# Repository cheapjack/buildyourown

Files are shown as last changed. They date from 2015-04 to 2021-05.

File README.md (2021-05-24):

# DesktopProsthetics
### 4th June - 31st August 2015 at [FACT](https://www.fact.co.uk/artwork/desktop-prosthetics-2015)
**Gallery 1, FACT, 88 Wood Street, Liverpool, L1 4DQ**

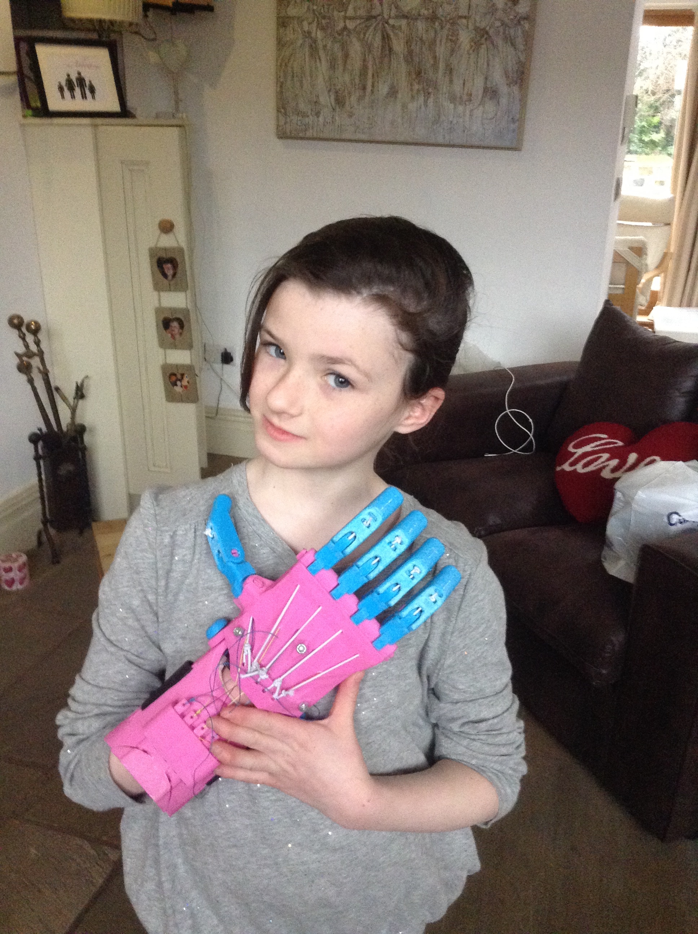
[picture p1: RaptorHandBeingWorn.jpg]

Image Copyright Jason Abbott.
### Copy:

###[DoESLiverpool](http://doesliverpool.com "DoESLiverpool's Homepage") will develop an iteration of the [Enabling the Future](http://enablingthefuture.org/upper-limb-prosthetics/the-raptor-hand/ "Enabling The Future Website") project within the Build Your Own Show at FACT. DoESLiverpool is a community of makers and entrepreneurs in Liverpool, with a Co-Working space, Workshop and Event Hub. It’s a place to work, learn, share ideas, form groups and make things the way you want to for small fees or initially, cake.

###DoES will be lead creative technologists to help setup, facilitate and support a ‘production line’ area for Build Your Own introducing the idea of 3D printing open source designs of upper limb prosthetics. It's inspired by a local family who used DoESLiverpool's workshop to print hand parts independently.

###Over the course of the exhibition FACT Gallery Assistants and DoESLiverpool will assist the public in testing and building 3D printed prosthetic devices. The public will have the opportunity to play, experiment and understand what prosthetics are and how access to rapid prototyping and open source digital making tools can help people make the world the way they want it.

## Information on this Repository:

Project management, help and files for the 3D printed prosthetic hand project
* *Most questions* [answered on our Frequently Asked Questions Page](https://github.com/cheapjack/buildyourown/blob/master/FAQ.md) which is being updated as needs arise.
* [Issues](https://github.com/cheapjack/buildyourown/issues "github issues for the project") to aid @cheapjack @amcewen and @defproc management of the project and information
* [copy as README.md files](https://github.com/cheapjack/buildyourown/tree/master/events) for publicity in the events folder
* Other useful information and files like model parts

We are also collecting related information - links, pictures, etc. - over on the [Desktop Prosthetics tumblr](http://desktopprosthetics.tumblr.com/)

### Issues:

The issue list is a place to track what needs to be done.  Creating and closing them is cheap, so make liberal use of them :-)

It's easy to see which issues need addressing by looking at the [open issue list](https://github.com/cheapjack/buildyourown/issues) but there are other ways to slice and dice things.  Issues get [labelled](https://github.com/cheapjack/buildyourown/labels) as a way to group them together - feel free to create new labels as and when needed.  And there are a few [milestones](https://github.com/cheapjack/buildyourown/milestones) to mark when issues have to be finished.  Use milestones for things that '''have''' to be done before a set event, rather than for "it'd be lovely if this was done by date X", as that just clutters things up if the deadline isn't hit.

Some more useful labels:
 * [Exhibits](https://github.com/cheapjack/buildyourown/labels/Exhibits)  Anything relating to the exhibits themselves
 * [Graphics](https://github.com/cheapjack/buildyourown/labels/Graphics)  Anything relating to the wall text, images, and data visualisation
 * [Set design](https://github.com/cheapjack/buildyourown/labels/Set%20design)  Issues relating to the 3d design of the exhibition
 * [Liverpool](https://github.com/cheapjack/buildyourown/labels/Liverpool)  Anything related specifically to the exhibition at FACT
 * [Norwich](https://github.com/cheapjack/buildyourown/labels/Norwich)  Anything related specifically to the exhibition at Norwich Castle

For some more background on good practice when using issues, read http://ben.balter.com/2014/11/06/rules-of-communicating-at-github/.  It's about Github's culture and process rather than exactly how we're running things, but there's plenty of crossover.

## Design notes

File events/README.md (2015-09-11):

## Files and copy for events as .md files per event

### Refer to the [Calendar](http://bit.ly/prostheticscal "Link to calendar for events at DesktopProsthetics, note the scal bit") for latest dates and times

FACT Liverpool events:
 * [Measuring Up](MeasuringUpWorkshop.md) **Saturday 6th June** 
 * [What's your superpower? A Prosthetic Hack!](ProstheticHack.md) **Saturday 25th July** [FACT link](http://fact.co.uk/whats-on/current/does-what-s-your-super-power-a-prosthetic-hack.aspx) 
 * [Assembly workshop](Assemblyworkshop.md) **Saturday 8th August** & **Saturday 22nd August**
 * [DoES does Prosthetics Day](https://github.com/cheapjack/buildyourown/blob/master/events/DoESdoesProsthetics.md) at DoES Liverpool **Saturday 15th August 2015** 
 * [DoES does Prosthetics Day 2](https://github.com/cheapjack/buildyourown/blob/master/events/DoESdoesProsthetics2.md) at DoES Liverpool **Saturday 17th October 2015** 
* [x] event dates signed off

**Norwich Castle events to be defined, arranged, etc. by the Norwich partners.**

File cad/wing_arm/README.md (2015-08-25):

### Wing and RIT-Arm models

src files for the Wing and RIT-Arm experimnets

#### Notes

I'm not sure what's best way of scaling? **eg** I've found if I take the generated `undies-manual`, and I scale it by 1.2 uniformly as below it 'looks' right in Openscad:

```
//joint interface

wingscalar = 1.2;

scale([wingscalar,wingscalar,wingscalar])translate([wingposx, wingposy, wingposz])import ("/Users/Power5/buildyourown/cad/experiments/RaptorWingAdaptiveGripExperiment/elbow_joint_interface_right.stl", convexity = 3);

```

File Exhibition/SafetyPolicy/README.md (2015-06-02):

# Safety Policy and Other Guidelines

## Place for safety guidelines from e-NABLE

### e-NABLE Device Safety Guidelines Statement

Based on preliminary testing and observations on the functionality and capabilities of our experimental 3D printed prosthetic devices it is felt that they are currently not safe for operation of heavy machinery, tools, equipment, and vehicles due to low grip strength development. These prosthetic devices have shown, however, to provide some functionality for gross grasp activities of light and pliable objects, but it is in no way a substitute for a fully functioning hand. In addition, we don’t recommend the use of our experimental 3D printed prosthetic devices for small children (i.e., under 3 years of age) due to greater fall rate and the need of sensory input through oral stimulation. Furthermore, it is unknown if our experimental 3D printed prosthetic devices are able to sustain a small child’s bite without breaking. Please review and consider the following recommendations and precautions regarding the 3D printed prosthetic device

### General Recommendations for experimental 3D printed prosthetic device

### Physical Safety

 * Work with your doctor or medical professional for appropriate use and wearing schedule of your experimental 3D printed prosthetic device.
 * These devices are made with low temperature plastic and should not be exposed to temperatures over 120° degrees.  A 3D printed prosthetic device left in a car on a hot day may be damaged.
 * With any prosthetic there is a possibility to develop pressure sores. If redness develops after wearing for the 15-20 minute trial please contact provider of the device, to reevaluate fit. If redness persists please contact your healthcare provider.
 * Monitor your device for wear and tear and contact your provider for assistance with replacing worn or broken parts.
 * Users should assume that the device could break at any moment, even while using it for tasks that have worked in the past, because the rate at which the plastic parts fatigue and need to be replaced is unknown.
 * Do not use the device to lift boiling water off the stove (e.g. cooking pasta) or to lift dishes of very hot food out of a microwave oven or out of a hot oven or any other situation in which a failure of the experimental device could cause injury indirectly if the hot material is dropped or spilled.

### Health Safety

 * Allow the mechanical hand breathing room as excessive sweat and other components may cause poor hygiene and lead to skin problems.
 * The use of a prosthetic sock is recommended for individuals with sensitive skin.
    Make sure you have no allergic reactions to the material used to print the mechanical hand or any other component.
    Make sure the mechanical hand is comfortable.
    Ensure the mechanical hand is functioning for the correct purpose.
    Start using the hand in a progressive manner. If the muscles of your wrist joint are tired, it would be a good idea to take a break and continue using the mechanical hand the next day.

### Child Safety

 * The child needs to be supervised at all times while using these mechanical hands.
 * Young children cannot be trusted to watch out for the Health Safety items listed above.  It is the responsibility of the caretaker to check for any problems with the child using an experimental 3D printed prosthetic device.
 * Let the child use/play with the device in a very conservative, progressive schedule:  just 5-10 minutes at a time, or even less.  If the child likes the device and is eager to use it, let them work up to using it for longer periods of time gradually.  Talk with a pediatrician or other medical professional about how much use is safe for the child, and what other problems to watch out for.
 * If your child feels pain on the wrist or elbow joint, please stop using the mechanical hand. This may be a sign of an overuse injury.
 * If any component of the mechanical hand breaks, please stop using it.
 * Ensure that the hardware and other moving parts are not loose, especially for children young enough to be at risk of choking on foreign objects.
 * The use of the 3D printed prosthetic device should be coordinated with the child’s teacher and health care providers.
 * The 3D printed prosthetic device is not made for weight-bearing or supporting body weight, so outdoor or rough play with the prosthetic should be closely monitored.
 * Children who are not walking or are unsteady on their feet may not be appropriate for this device as falling on the 3D printed prosthetic device may result in further injury.

### Cleaning instructions:

The 3D printed prosthetic device can be surface cleaned with warm water and a mild detergent.  If an odor develops on the device, cleaning with shaving cream may help to dissipate the odor.  If Velcro straps become worn or ineffective, please contact the provider of your prosthetic hand for replacement.

### DesktopProsthetics, DoES Liverpool & FACT Release and Waiver of Liability and Hold Harmless Agreement:

You acknowledge that you understand the context of the **DoESLiverpool CIC** and **FACT** project **"Desktop Prosthetics"** that uses the open source design "Raptor Hand Reloaded" from the e-NABLE Community Foundation (“Foundation”); a non-profit foundation to encourage the development and dissemination of prosthetics for children and adults using 3D printing technology. 
**DoESLiverpool CIC ("DoESLiverpool")** and **FACT (Foundation for Art and Creative Technology) ("FACT") generally **do not** create the design or plans (“Designs”) **but**  print the components, assemblies and final prototype prosthetics based on the Designs (“Components”), They **do not** certify that the Designs or Components or assembled prototype prosthetics operate properly or satisfy any regulatory requirements.

Members of the DoESLiverpool Community, FACT Gallery Guides and a community of people around the **DesktopProsthetics** project following a Measuring Workshop agree to use the assembled components as prototype prosthetics, 3D printed at the DesktopProsthetics exhibition at the FACT show "Build Your Own: Tools for sharing" and follow all recommendations and safety guidelines here.

This Release and Waiver of Liability and Hold Harmless Agreement (“Agreement”) is meant to reflect the limited role of DoESLiverpool and FACT in the development and manufacture of the Design and Components and subsequent assembled prototype prosthetics. The person signing below (“You”) is either the individual recipient of the Design or Component if the individual recipient is an adult under the laws of the relevant jurisdiction or the parent or legal guardian of the child if the individual recipient is a child under the laws of the relevant jurisdiction.

You agree that any Design or Component furnished to me by the DesktopProsthetics project or by any individual associated with DoESLiverpool and FACT is provided “AS IS” and **without representations or warranties of any kind, express or implied, and is intended to be a gift**.  By accepting any Design or Component, I further acknowledge that such Design or Component, has not been evaluated or approved by any regulatory authority.  Generally, the Design has been developed by a person or a company who may be a member of the e-NABLE community, DoESLiverpool or FACT but is not an employee or contractor of the above. 

You understand that any Design, Assembled prototype prosthetic or Component furnished by the DesktopProsthetics is meant to benefit an individual recipient who has need of an assistive hand technology, and is not intended, and shall not be used, for commercial use.  If You are an adult under the laws of the relevant jurisdiction and are the individual recipient, You acknowledge that You understand the potential risks of the use of the Design or Component and expressly assume such risks.  If the individual recipient is a child under the laws of the relevant jurisdiction, You represent that You are the parent or legal guardian of the child and that You understand the potential risks of the use of the Design or Component and expressly assume such risks on behalf of the individual recipient.

Furthermore, You (either for yourself or your child)  release and forever discharge DoESLiverpool and FACT and their  officers, employees, contractors, subcontractors, volunteers and agents (“Releasees”) from any and all liability for acts or omissions— including negligent acts or omissions—causing damage, loss, injury, or death to the individual recipient from the use of the Design or the Component. You agree to defend, indemnify and hold the Releasees harmless from any and all liability or loss— including liability for negligence—arising in conjunction with or resulting from the individual recipient’s use of a Design or Component (including all legal/representation fees and expenses incurred by the Releasees).

You further understand and agree that the Foundation and any individual associated with the Foundation shall not be liable for any injuries or damages, including any consequential, incidental, indirect, punitive or special damages, resulting from or arising out of the use of the Design or Component provided by DoESLiverpool, FACT or any individual associated with the associated parties.

Any information provided by DoESLiverpool and any individual associated is not intended to be used or relied upon to diagnose or treat a health problem or disease and DoESLiverpool makes no claims regarding the Design or the Components.  You should consider consulting with a qualified health care provider prior to fitting the Component.  Carefully read all labels and heed all directions and cautions that accompany the Components.  Any statements made by DoESLiverpool are for informational purposes only and are not meant to replace the services or recommendations of a physician or other qualified health care practitioner.

You acknowledge that this Agreement is governed by UK law (without reference to its conflict of law provisions) and the parties intend that this Agreement to be as broad and inclusive as permitted by UK law. If any portion of this Agreement is found to be invalid for any reason, the remainder of the Agreement shall continue to remain in full force and effect and shall continue to be binding in all cases.

You have carefully read the foregoing provisions and understand their contents.

Signed

Signature  ______________________  Print Name  ___________________________ Date:__________

### e-NABLE Release and Waiver of Liability and Hold Harmless Agreement:

You acknowledge that you understand that the e-NABLE Community Foundation (“Foundation”) is a non-profit foundation to encourage the development and dissemination of prosthetics for children and adults using 3D printer technology.  The Foundation generally does not create the design or plans (“Designs”) nor manufacture or print the components, assemblies or final prosthetics based on the Designs (“Components”), nor does it certify the Designs or Components operate properly or satisfy any regulatory requirements.  This Release and Waiver of Liability and Hold Harmless Agreement (“Agreement”) is meant to reflect the limited role of the Foundation in the development of the Design and Components. The person signing below (“You”) is either the individual recipient of the Design or Component if the individual recipient is an adult under the laws of the relevant jurisdiction or the parent or legal guardian of the child if the individual recipient is a child under the laws of the relevant jurisdiction.

You agree that any Design or Component furnished to me by the Foundation or by any individual associated with the Foundation is provided “AS IS” and without representations or warranties of any kind, express or implied, and is intended to be a gift.  By accepting any Design or Component, I further acknowledge that such Design or Component, has not been evaluated or approved by any regulatory authority.  Generally, the Design has been developed by a person or a company who may be a member of the e-NABLE community but is not an employee or contractor of the Foundation. Similarly, the Component has generally not been manufactured or printed by a person or company who is a member of the e-NABLE community but once again is not an employee or independent contractor of the Foundation.

You understand that any Design or a Component furnished by the Foundation is meant to benefit an individual recipient who has need of an assistive hand technology, and is not intended, and shall not be used, for commercial use.  If You are an adult under the laws of the relevant jurisdiction and are the individual recipient, You acknowledge that You understand the potential risks of the use of the Design or Component and expressly assume such risks.  If the individual recipient is a child under the laws of the relevant jurisdiction, You represent that You are the parent or legal guardian of the child and that You understand the potential risks of the use of the Design or Component and expressly assume such risks on behalf of the individual recipient.

Furthermore, You (either for yourself or your child)  release and forever discharge the Foundation and its  officers, employees, contractors, subcontractors, volunteers and agents (“Releasees”) from any and all liability for acts or omissions— including negligent acts or omissions—causing damage, loss, injury, or death to the individual recipient from the use of the Design or the Component. You agree to defend, indemnify and hold the Releasees harmless from any and all liability or loss— including liability for negligence—arising in conjunction with or resulting from the individual recipient’s use of a Design or Component (including all attorney’s fees and expenses incurred by the Releasees).

You further understand and agree that the Foundation and any individual associated with the Foundation shall not be liable for any injuries or damages, including any consequential, incidental, indirect, punitive or special damages, resulting from or arising out of the use of the Design or Component provided by the Foundation or any individual associated with the Foundation.

Any information provided by the Foundation and any individual associated with the Foundation is not intended to be used or relied upon to diagnose or treat a health problem or disease and the Foundation makes no claims regarding the Design or the Components.  You should consider consulting with a qualified health care provider prior to fitting the Component.  Carefully read all labels and heed all directions and cautions that accompany the Components.  Any statements made by the Foundation are for informational purposes only and are not meant to replace the services or recommendations of a physician or other qualified health care practitioner.

You acknowledge that this Agreement is governed by the laws of the State of Delaware (without reference to its conflict of law provisions) and the parties intend that this Agreement to be as broad and inclusive as permitted by law. If any portion of this Agreement is found to be invalid for any reason, the remainder of the Agreement shall continue to remain in full force and effect and shall continue to be binding.

You have carefully read the foregoing provisions and understand their contents.

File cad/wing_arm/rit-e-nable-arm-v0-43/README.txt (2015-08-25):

Arm.iam is the master assembly Inventor file.

The other files are subassemblies required by Arm.iam, and open-able independently.

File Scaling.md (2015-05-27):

## Linear Scaling 

The main measurement used in sizing the Raptor Reloaded is the width of the recipient's complete hand at the knuckles. At 100% scale, the palm of the Raptor Reloaded measures 55mm at its widest point. To get the appropriate linear scaling factor for scaling the STLs, add 5mm (to account for the thickness of padding in the printed palm) to the width of the recipient's complete hand at its widest point. Divide this number by 55 to get the scaling factor for the STLs. For example, if the palm is 65mm wide, then 65 + 5 = 70, and 70 / 55 = 1.27, so the scaling multiplier would be 1.27 or 127%. Make sure to apply the scaling factor to all of the parts to ensure that they fit together. At higher scales, the clearances between the moving parts of the hand will grow, so glue or other modifications may be necessary to ensure that all the pieces stay secured to each other.

## Recommended Printing Settings

 * PLA (or ABS, PET, Nylon)
 * 0.2mm layers
 * 0.8mm shell thickness (2 shells)
 * 35% infill
 * Active cooling fan on

## Additional Materials

The Raptor Reloaded requires some additional hardware to assemble, most of which can be sourced from the Hardware Sources page on the e-NABLE website.

 * 4ft Velcro, double-sided (2” wide)
 * 8ft Non-elastic nylon cord, 0.9mm-1.0mm
 * 5ft Flexible elastic cord
 * 5x Tensioner screws (*it's no clear which size these should be*) 
 * 4x Palm velcro attachment screws
 * 12" (305mm) Firm Foam Padding (5 ¾” wide)
 * 5x Lee Tippi Micro Gel Fingertip Grips (optional)

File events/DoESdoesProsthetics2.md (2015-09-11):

# DoES does Prosthetics Day 2

Baylee & Jason printing for the BBC no.2

### Saturday 17th October 2015 12.30pm - 4pm
### DoESLiverpool, The Gostins Building, 4th Floor, left from lift, 32-36 Hanover Street. Liverpool L1 4LN

#### Free no booking required

### Meeting following on from the **DesktopProsthetics** project

**Age 3 and above, children accompanied by an adult**
#### DoESLiverpool and project participnats will be helping Assemble, test, adjust and fit more printed hands from the DesktopProsthetics Project

## Workshop activity
* Re-Introduction to project
* Re-Connecting to e-NABLE
* Learning how to assemble a raptor hand
* Test and fit hands
* Log any issues and improvements required for the hands
* Propose another meet up and discuss ways of sustaining the community; and basics of communication using either Google Groups or [Meetup](http://www.meetup.com/)

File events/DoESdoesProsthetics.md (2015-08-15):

# DoES does Prosthetics Day

Baylee & Jason printing for the BBC

### Saturday 15th August 2015 12.30pm - 4pm
### DoESLiverpool, The Gostins Building, 4th Floor, left from lift, 32-36 Hanover Street. Liverpool L1 4LN

#### Free no booking required

### Meeting following on from the Measuring, Hacking and Assembly workshops for **DesktopProsthetics**

**Age 3 and above, children accompanied by an adult**
#### DoESLiverpool and project participnats will be helping Assemble, test, adjust and fit more printed hands from the DesktopProsthetics Project

## Workshop activity
* Re-Introduction to project
* Connecting to e-NABLE
* Learning how to assemble a raptor
* Test and fit hands
* Log any issues and improvements required for the hands
* Propose another meet up and discuss running an interest group / club or Prosthetic Evenings/Saturdays

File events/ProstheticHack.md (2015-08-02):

# What's Your SuperPower? - A Prosthetic Hack!

[Book on the FACT website here](http://fact.co.uk/whats-on/current/does-what-s-your-super-power-a-prosthetic-hack.aspx)

Image source [Enabling the Future on Thingiverse](http://thingiverse-production-new.s3.amazonaws.com/renders/1d/20/95/d4/49/All_parts_at_100_right_single_build_plate_preview_featured.jpg) Licensed under [Attribution-ShareAlike 3.0 Unported (CC BY-SA 3.0)](http://creativecommons.org/licenses/by-sa/3.0/ "License Link")

## Saturday 25th July FACT Gallery 1 12pm-4.30pm FREE
**Age 3 and above, children accompanied by an adult**

## DoESLiverpool will be hosting a prosthetic hackday exploring how the **DesktopProsthetics** project, part of Build Your Own, can be hacked and modified to explore the diversity of prosthetic design. 
### The Raptor hand used in **DesktopProsthetics** is a general pick up and place prosthetic but with rapid prototyping tools like 3D printing can we develop modifications or 'hacks' for the reality of unique users? What prosthetics could we make for hiphop MC's, dancers, mathematicians, event organisers, farmers, gallery assistants or engineers?  We will explore prosthetic hand design as a group then prototype and present our co-designs.

We will also be looking at how to adapt the Raptor Re-Loaded for those families with no conventional working wrist joint. Take part in co-design and simple making activity and explore 3D generation tools from [OpenSCAD](http://www.openscad.org/) to **Lego®** 

http://enablingthefuture.org/upper-limb-prosthetics/the-raptor-hand/
http://doesliverpool.com

 * [x] Copy signed off

### Workshop Activity
* Look at prosthetic design
* Explore unique user applications
* Explore human centred and activity centred co-design
* Modify and prototype new designs
* Explore different design tools
* Present & document prototypes, printing where possible.

### Prep
 * Try adding some Lego connectors to a hand and print it out.  [Parametric Lego model in OpenSCAD](http://www.thingiverse.com/thing:178627)
 * Increase height of Top-side Lego 'teeth' in [OpenSCAD](http://www.openscad.org/) for better fit with **official LEGO®**
 * Print a few part from the [Universal Construction Kit](http://www.thingiverse.com/uck/designs) for fun
 * Find a few compatible *other building systems* to fit the UCK stuff
 * Have an instance of OnShape to play with
 * Have the Printcraft server for young people to play on
 * Simple examples of using [OpenSCAD](http://www.openscad.org/)
 * Source some FACT laptops (say 2)

### Checklist

 * [ ] Wallpaper cover paper
 * [ ] Masking Tape
 * [ ] Pens & Paper
 * [ ] Superglue
 * [ ] Post-it Notes
 * [ ] Freshly Printed Lego Finger adaptors
 * [ ] OnShape
 * [x] OpenSCAD
 * [x] Lego technic
 * [x] 2 MacBooks (FACT)
 * [x] Flipchart (FACT)
 * [x] Minecraft (FACT)

### Background Information
 * http://rewalk.com/rewalk-personal-3/
 * http://www.theguardian.com/artanddesign/architecture-design-blog/2015/jul/22/lego-prosthetic-arm-that-kids-can-hack-themselves
 * http://www.openbionics.org/
 * http://news.harvard.edu/gazette/story/2015/06/a-new-grasp-on-robotic-glove/
 * http://www.engadget.com/2015/03/13/3d-printed-iron-man-gauntlet-becomes-a-kids-awesome-bionic-arm/

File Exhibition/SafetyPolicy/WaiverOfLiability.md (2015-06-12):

## DesktopProsthetics, DoES Liverpool & FACT Safety Guidelines 
## Release & Waiver of Liability and Hold Harmless Agreement

If you are taking part in the **measuring workshop** on the **6th June 2015** at **FACT**, Liverpool, you agree to read, sign and keep a copy of the following **Safety Guidelines** provided by **e-NABLE** the source of the **Raptor-Reloaded prosthetic prototype design** and the **DoESLiverpool** and **FACT Waiver of Liability agreement** 

### e-NABLE Device Safety Guidelines Statement

Based on preliminary testing and observations on the functionality and capabilities of our experimental 3D printed prosthetic devices it is felt that they are currently not safe for operation of heavy machinery, tools, equipment, and vehicles due to low grip strength development. These prosthetic devices have shown, however, to provide some functionality for gross grasp activities of light and pliable objects, but it is in no way a substitute for a fully functioning hand. In addition, we don’t recommend the use of our experimental 3D printed prosthetic devices for small children (i.e., under 3 years of age) due to greater fall rate and the need of sensory input through oral stimulation. Furthermore, it is unknown if our experimental 3D printed prosthetic devices are able to sustain a small child’s bite without breaking. Please review and consider the following recommendations and precautions regarding the 3D printed prosthetic device

### General Recommendations for experimental 3D printed prosthetic device

### Physical Safety

 * Work with your doctor or medical professional for appropriate use and wearing schedule of your experimental 3D printed prosthetic device.
 * These devices are made with low temperature plastic and should not be exposed to temperatures over 120° degrees.  A 3D printed prosthetic device left in a car on a hot day may be damaged.
 * With any prosthetic there is a possibility to develop pressure sores. If redness develops after wearing for the 15-20 minute trial please contact provider of the device, to reevaluate fit. If redness persists please contact your healthcare provider.
 * Monitor your device for wear and tear and contact your provider for assistance with replacing worn or broken parts.
 * Users should assume that the device could break at any moment, even while using it for tasks that have worked in the past, because the rate at which the plastic parts fatigue and need to be replaced is unknown.
 * Do not use the device to lift boiling water off the stove (e.g. cooking pasta) or to lift dishes of very hot food out of a microwave oven or out of a hot oven or any other situation in which a failure of the experimental device could cause injury indirectly if the hot material is dropped or spilled.

### Health Safety

 * Allow the mechanical hand breathing room as excessive sweat and other components may cause poor hygiene and lead to skin problems.
 * The use of a prosthetic sock is recommended for individuals with sensitive skin.
    Make sure you have no allergic reactions to the material used to print the mechanical hand or any other component.
    Make sure the mechanical hand is comfortable.
    Ensure the mechanical hand is functioning for the correct purpose.
    Start using the hand in a progressive manner. If the muscles of your wrist joint are tired, it would be a good idea to take a break and continue using the mechanical hand the next day.

### Child Safety

 * The child needs to be supervised at all times while using these mechanical hands.
 * Young children cannot be trusted to watch out for the Health Safety items listed above.  It is the responsibility of the caretaker to check for any problems with the child using an experimental 3D printed prosthetic device.
 * Let the child use/play with the device in a very conservative, progressive schedule:  just 5-10 minutes at a time, or even less.  If the child likes the device and is eager to use it, let them work up to using it for longer periods of time gradually.  Talk with a pediatrician or other medical professional about how much use is safe for the child, and what other problems to watch out for.
 * If your child feels pain on the wrist or elbow joint, please stop using the mechanical hand. This may be a sign of an overuse injury.
 * If any component of the mechanical hand breaks, please stop using it.
 * Ensure that the hardware and other moving parts are not loose, especially for children young enough to be at risk of choking on foreign objects.
 * The use of the 3D printed prosthetic device should be coordinated with the child’s teacher and health care providers.
 * The 3D printed prosthetic device is not made for weight-bearing or supporting body weight, so outdoor or rough play with the prosthetic should be closely monitored.
 * Children who are not walking or are unsteady on their feet may not be appropriate for this device as falling on the 3D printed prosthetic device may result in further injury.

### Cleaning instructions:

The 3D printed prosthetic device can be surface cleaned with warm water and a mild detergent.  If an odor develops on the device, cleaning with shaving cream may help to dissipate the odor.  If Velcro straps become worn or ineffective, please contact the provider of your prosthetic hand for replacement.

## DesktopProsthetics, DoES Liverpool & FACT Release and Waiver of Liability and Hold Harmless Agreement:

You acknowledge that you understand the context of the **DoESLiverpool CIC** and **FACT** project **"Desktop Prosthetics"** that uses the open source design "Raptor Hand Reloaded" from the e-NABLE Community Foundation (“Foundation”); a non-profit foundation to encourage the development and dissemination of prosthetics for children and adults using 3D printing technology. 
**DoESLiverpool CIC ("DoESLiverpool")** and **FACT (Foundation for Art and Creative Technology) ("FACT") generally **do not** create the design or plans (“Designs”) **but**  print the components, assemblies and final prototype prosthetics based on the Designs (“Components”), They **do not** certify that the Designs or Components or assembled prototype prosthetics operate properly or satisfy any regulatory requirements.

Members of the **DoESLiverpool** Community,**FACT** Gallery Guide volunteers and a community of people around the **DesktopProsthetics** project following a **Measuring Workshop** agree to use the assembled components as prototype prosthetics, 3D printed at the **DesktopProsthetics** exhibition at the **FACT** show **"Build Your Own: Tools for sharing"** and follow all recommendations and safety guidelines here. 

This Release and Waiver of Liability and Hold Harmless Agreement (“Agreement”) is meant to reflect the limited role of **DoESLiverpool** and **FACT** in the development and rapid prototyping with 3D printers of the Design and Components and subsequent assembled prototype prosthetics. The person signing below (“You”) is either the individual recipient of the Design or Component if the individual recipient is an adult under the laws of the relevant jurisdiction or the parent or legal guardian of the child if the individual recipient is a child under the laws of the relevant jurisdiction.

You agree that any Design or Component furnished to me by the **DesktopProsthetics** project or by any individual associated with **DoESLiverpool** and **FACT** is provided “AS IS” and **without representations or warranties of any kind, express or implied, and is intended to be a gift**.  By accepting any Design or Component, I further acknowledge that such Design or Component, has not been evaluated or approved by any regulatory authority.  Generally, the Design has been developed by a person or a company who may be a member of the **e-NABLE** community, but not an employee or contractor of the above. 

You understand that any Design, Assembled prototype prosthetic or Component furnished by the **DesktopProsthetics** project is meant to benefit an individual recipient who has need of an assistive hand technology, and is not intended, and shall not be used, for commercial use.  If You are an adult under the laws of the relevant jurisdiction and are the individual recipient, You acknowledge that You understand the potential risks of the use of the Design or Component and expressly assume such risks. 
If the individual recipient is a child under the laws of the relevant jurisdiction, You represent that You are the parent or legal guardian of the child and that You understand the potential risks of the use of the Design or Component and expressly assume such risks on behalf of the individual recipient.

Furthermore, You (either for yourself or your child)  release and forever discharge **DoESLiverpool** and **FACT** and their  officers, employees, contractors, subcontractors, volunteers and agents (“Releasees”) from any and all liability for acts or omissions — including negligent acts or omissions—causing damage, loss, injury, or death to the individual recipient from the use of the Design or the Component. You agree to defend, indemnify and hold the Releasees harmless from any and all liability or loss— including liability for negligence—arising in conjunction with or resulting from the individual recipient’s use of a Design or Component (including all legal/representation fees and expenses incurred by the Releasees).
You further understand and agree that the **e-NABLE Foundation**, **DoESLiverpool**, **FACT** and any individual associated with the aforementioned shall not be liable for any injuries or damages, including any consequential, incidental, indirect, punitive or special damages, resulting from or arising out of the use of the Design or Component provided by **DoESLiverpool**, **FACT** or any individual associated with the aforementioned parties.

Any information provided by **DoESLiverpool**, **FACT** and any individual associated is not intended to be used or relied upon to diagnose or treat a health problem or disease and **DoESLiverpool**, **FACT** make no claims regarding the Design or the Components.  You should consider consulting with a qualified health care provider prior to fitting the Component.  Carefully read all labels and heed all directions and cautions that accompany the Components.  Any statements made by **DoESLiverpool** and **FACT** are for informational purposes only and are not meant to replace the services or recommendations of a physician or other qualified health care practitioner.

You acknowledge that this Agreement is governed by UK law (without reference to its conflict of law provisions) and the parties intend that this Agreement to be as broad and inclusive as permitted by UK law. If any portion of this Agreement is found to be invalid for any reason, the remainder of the Agreement shall continue to remain in full force and effect and shall continue to be binding in all cases.

**You the undersigned have carefully read the foregoing provisions and all the information above and understand their contents and contexts.**

**Signed**

###Signature  ____________________________________________  

###Print Name  ____________________________________________ 

###Date:____________________________________________

###Email contact ____________________________________________ 

###Phone/Mobile Contact ____________________________________________

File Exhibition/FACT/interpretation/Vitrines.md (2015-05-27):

##Vitrines Notes

###Artwork for Vitrines

Orientation and artwork for Vitrine plinths in space, *unfinished*
Mix of cut vinyl in project typeface cut at DoES by @cheapjack

PDF plus svg. Uses [Inconsolate-LGC open font](http://openfontlibrary.org/en/font/inconsolata-lgc)

 * [x] Got typeface
 * [ ] Design Complete
 * [ ] Cut ready for application

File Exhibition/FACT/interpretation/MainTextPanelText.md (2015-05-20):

***Desktop Prosthetics (2015)***
DoESLiverpool: Ross Dalziel, Patrick Fenner and Adrian McEwen
 
***DoESLiverpool*** presents an iteration of the open-source project e-NABLE, a global network of passionate volunteers using 3D printing to make prosthetic hands. Inspired by a local family who used DoESLiverpool's workshop to print hand parts, DoES has installed a ‘production line’ for prosthetic hands. They will be 3D printing the open-source Raptor Hand design, which is more of a tool rather than a fully functional prosthetic device, developed to make printing and assembly of the hand’s components as simple as possible.
 
***Desktop Prosthetics*** aims to raise awareness of some of the practical uses of 3D printing and to demonstrate how collaborative communities like DoES and e-NABLE work, sharing skills and specialised knowledge to solve problems.
 
Over the course of the exhibition, DoESLiverpool will be working with ***Reach***, the association for children with upper limb deficiency, to help a number of local children build and assemble a prosthetic device. DoES invites you to get involved with testing and building prosthetics, to better understand what prosthetics are, and to see how access to rapid prototyping and open-source digital-making tools can help people make the world the way they want it. Check the events panel for more details on how to take part.
 
**Developed with the support of Reach and e-NABLE.**
 
www.doesliverpool.com
www.enablingthefuture.org
www.reach.org.uk

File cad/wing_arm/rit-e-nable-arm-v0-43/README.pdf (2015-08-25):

# RIT e-NABLE Arm v0.43

## By: (e-NABLE) License: Creative Commons - Attribution Share Alike Published on: Jul 31, 2014 Located at: http://www.youmagine.com/designs/rit-e-nable-arm-v0-43 Excerpt:

The Derek Arm is an elbow-actuated variant of an RIT-developed e-NABLE prosthesis designed to fit Derek, the first user of our arm.

## Description:

<p>The Derek Arm is an elbow-actuated variant of an RIT-developed e-NABLE prosthesis designed to fit Derek, the first user of our arm. &nbsp;As illustrated below and in the video at , bending the elbow causes the fingers to flex by tightening strings descending from the fingers to tensioners in the upper arm.<a target="_blank" rel="nofollow" href="http://www.youtube.com/watch?v=T9nngOrdPkg">http://www.youtube.com/watch?v=T9nngOrdPkg</a> The "Documents" tab
contains STL and Inventor files. Start by reading the Readme at: https://docs.google.com/a/g.rit.edu/document/d/1uEomoBOTEfTNRHCYmNr_5AkKPJv8TYJSbxhE4p5BYU8/edit

If you can, please use the online documentation found at http://www.youmagine.com/designs/rit-e-nable-arm-v0-43 because those may have been be updated. Also, there you can interact and provide
praise and/or feedback.

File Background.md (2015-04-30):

# What is the Desktop Prosthetics project?

## Overview

For a synopsis of the project, the [README.md](https://github.com/cheapjack/buildyourown/blob/master/README.md) is best.  This document is to give more background and explanation of the project for us to share with partners and other interested parties (e.g. press) for more in-depth info.

## What?

## Who?

The project is being led by the maker community of [DoES Liverpool](http://doesliverpool.com).  Specifically, [Ross Dalziel](http://cheapjackprojects.tumblr.com/), [Adrian McEwen](http://www.mcqn.com) and [Patrick Fenner](http://www.deferredprocrastination.co.uk/).

Collaborators and partners:
 * [FACT](http://www.fact.co.uk)
 * [Crafts Council](http://www.craftscouncil.org.uk)
 * [Norwich Castle Museum & Art Gallery](http://www.museums.norfolk.gov.uk/Visit_Us/Norwich_Castle/index.htm)
 * [Norwich Hackspace](http://norwichhackspace.org/)
 * [Reach](http://reach.org.uk)
 * [Enabling the Future](http://enablingthefuture.org/)

## Where and When?

 * Thursday 4th June Opening-August 2015: FACT, Liverpool
 * Artist/Organiser Talks Friday 5th June
 * October 2015-January 2016: Norwich Castle Museum & Art Gallery, Norwich

During the exhibitions there will be a series of workshops.  These will be open to all and cover a range of activities - measuring and then assembling hands for members of the Reach community; and exploring new possibilities offered by the inherent personalisation provided by 3d-printed manufacturing techniques.  Details of the events are being developed in the [events section](https://github.com/cheapjack/buildyourown/tree/master/events) of our project management site.

## DoES Liverpool and makerspaces

What exactly is a makerspace? Using the term broadly, we’re talking about public spaces or small volunteer run membership organisations with different tools and equipment where people can go to independently make something or meet potentially like minded people. While we need to appreciate the diversity of these spaces, it’s also important to think beyond formalised networks (like Fab Labs) and focus on spaces defined by a specific ethos (like Hackspaces).
So Fab Labs have similar facilities in common with maker spaces and hackspaces but alot more formalised and less community led to a varying degree.
DoESLiverpool has things in common with say [HacMan](https://hacman.org.uk/) but also includes a co-working space to support their facilities and also is a home for not just making but tech culture in general supporting IoT Liverpool, Startup clups and coder dojo's all led and run by local(and not so local) interest groups/affiliates/organisers/hot deskers/permanent desk people or just members of the google group mailing list interested in running something.

Here are some useful links when thinking on maker/hackerspaces. Hannah Stewart has been doing some very detailed research into the area finally released here in alpha
http://www.nesta.org.uk/publications/open-dataset-uk-makerspaces-users-guide
also worth checking
http://www.hackspace.org.uk/wiki/Main_Page

DoESLiverpool like many makerspaces and hackspaces, as an organisation do not **do** projects in a sense, we simply help our community to realise their projects with the facilities we have. Our community is essentially anyone who wants to **do** something with us.

This collaboration with FACT was inspired from a local family printing a prosthetic hand in our workshop and the 3 members of the community leading the project have interests and skills in 3D printing, which is why it's happening. If nobody in the community wanted to do it, it would not happen.

If a group grows and develops around the activity in the exhibition then that group can continue to use DoESLiverpool to support it like the many diverse groups that call DoESLiverpool home.

Part of the deal of this project is that DoESLiverpool and Norwich Hackspace can keep the new larger 3D printers so that if people do need to print more hands in the future, we will have extended our facilities so that they can.

This is a common theme in many maker and hackerspaces: somebody donates or stores some kit permanently or temporarily and then often more and more people start to use it and interest groups can (but not always) build around things like this. Also there is a general openness across these spaces although at the same time a haven for people interested in certain things. 

For instance @cheapjack recently setup a small exchange between a hackerspace in Bochum, Germany [DasLabor](https://www.das-labor.org/?lang=de) and DoESLiverpool which you can see more about [here](http://wiki.doesliverpool.com/PublicEngineering). Like DoESLiverpool they are primarily a member led space for their community but do come together for events like DesktopProsthetics and Maker Faire UK to let the wider public know about what they do.

## Reach

> _**Get copy from Reach to explain who they are and what they do**_

## Enabling the Future

> _**Get copy from Enabling the Future media pack**_

## Norwich Hackspace

> _**Get copy from Norwich Hackspace**_

## FACT

The exhibition Build Your Own: Tools for Sharing premieres at FACT (Foundation for Art and Creative Technology) 4 June - 31 August and will explore how digital technologies come together with traditional processes of production to create new ways of working, sharing and collaborating. 

Co-produced by FACT, Crafts Council and Norfolk Museums Service, the exhibition will feature newly commissioned work by leading makers, creative technologists and collectives to be created in Liverpool and Norwich. The artists will work closely with FACT’s award-winning engagement strand to develop projects with various local groups and communities in both cities and provide a major programme of related events and workshops.

The wide range of projects that fit under the Build Your Own umbrella show that the nature of craft and DIY has changed drastically. The ability to make clothes, furniture and other household goods used to be absolutely necessary to provide for the family, but nowadays we are just as likely to create a website as to knit a sweater. New times call for new skills - but the old ones have an important role too. This exhibition will explore what the democratisation of digital tools really means, whom the emergence of new technologies will affect, and how traditional craft skills can connect with new digital tools.

The projects will be showcased through the exhibition at FACT, a series of creative interventions taking place across the city and an ambitious and inclusive public programme of talks, skill sharing workshops and maker hacks, a summer school for children and young people, a publication and a conference to be held in Norfolk. All activities intend to bring alive the joy of making.

## Crafts Council

> _**insert copy from press release**_

## Norwich Castle Museum & Art Gallery

> _**insert copy from press release**_

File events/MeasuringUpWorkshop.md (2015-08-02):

## Measuring Up Workshop

Image source [Enabling the Future on Thingiverse](http://thingiverse-production-new.s3.amazonaws.com/renders/1d/20/95/d4/49/All_parts_at_100_right_single_build_plate_preview_featured.jpg) Licensed under [Attribution-ShareAlike 3.0 Unported (CC BY-SA 3.0)](http://creativecommons.org/licenses/by-sa/3.0/ "License Link")
###Saturday 6th June FACT Gallery 1 12pm - 4.30pm FREE
**Age 3 and above, children accompanied by an adult**
### DoESLiverpool will be helping people learn how to measure up for the Raptor hand, an upper limb prosthetic hand and generate files for the DesktopProsthetic project to print.

 * [x] Copy signed off

# Workshop activity
* Introduction to the project 
* Measuring Up
* Outputting files 

## Workshop Plan

### Session 1
 * 12pm *Introduction by Jason Abbott, Baylee Abbott, Drew Murray, @amcewen @cheapjack @defproc*
 * 12.20pm *Notes on Health & Safety from Ross and Drew*
 * 12.30pm *Start measuring up with Drew, Jason & team*
 * *Measuring work flow*
   * Set size with calipers
   * Input into System & record

Printed? | No | Name | code-name | Affected Hand | Age | Left knuckles | Left Wrist | Right knuckles | Right Wrist | Unaffected Forarm length | Affected residual length | Affected elbow width | Palm Colour | Extremity Colour | Contact
------------ | ------------- |------------ | ------------- |------------ | ------------- |------------ | ------------- |------------ | ------------- |------------ | ------------- |------------ | ------------- |------------ | -------------
gasp-law | <ul><li>[x] </li>| <ul><li>[ ] </li>| <ul><li>[ ] </li>| <ul><li>[ ] </li>| <ul><li>[x] </li>| <ul><li>[ ] </li>| <ul><li>[ ] </li>| <ul><li>[ ] </li>| <ul><li>[x] </li>| <ul><li>[ ] </li>| <ul><li>[ ] </li>| <ul><li>[ ] </li>| <ul><li>[x] </li>| <ul><li>[ ] </li>| <ul><li>[ ] </li>   

   * Output files and log
   * Include participant details
   * Sign the Liability and Health & Safety Disclaimer
   * Understand 3dprint design tools like [OnShape](https://www.onshape.com/) and [OpenSCAD](http://www.openscad.org/) 
   * Understand the 3dprint process
   * Understand the design, the foam and velcro fittings
   * Understand e-NABLE network and pass on their details
   * Advise on DoES Community Day, Assembly workshop dates.
 *  1.45pm *Finish, Tidy up space for next group*

 ### Session 2
 * 2pm *Introduction by Jason Abbott, Baylee Abbott, Drew Murray, @amcewen @cheapjack @defproc*
 * 2.20pm *Notes on Health & Safety from Ross and Drew*
 * 2.30pm *Start measuring up with Drew, Jason & team*
 * *Measuring work flow*
   * Set size with calipers
   * Input into System & record

Printed? | No | Name | code-name | Affected Hand | Age | Left knuckles | Left Wrist | Right knuckles | Right Wrist | Unaffected Forarm length | Affected residual length | Affected elbow width | Palm Colour | Extremity Colour | Contact
------------ | ------------- |------------ | ------------- |------------ | ------------- |------------ | ------------- |------------ | ------------- |------------ | ------------- |------------ | ------------- |------------ | -------------
gasp-law | <ul><li>[x] </li>| <ul><li>[ ] </li>| <ul><li>[ ] </li>| <ul><li>[ ] </li>| <ul><li>[x] </li>| <ul><li>[ ] </li>| <ul><li>[ ] </li>| <ul><li>[ ] </li>| <ul><li>[x] </li>| <ul><li>[ ] </li>| <ul><li>[ ] </li>| <ul><li>[ ] </li>| <ul><li>[x] </li>| <ul><li>[ ] </li>| <ul><li>[ ] </li>

   * Output files and log
   * Include participant details
   * Sign the Liability and Health & Safety Disclaimer
   * Understand 3dprint design tools like [OnShape](https://www.onshape.com/) and [OpenSCAD](http://www.openscad.org/) 
   * Understand the 3dprint process
   * Understand the design, the foam and velcro fittings
   * Understand e-NABLE network and pass on their details
   * Advise on DoES Community Day, Assembly workshop dates.
 *  3.45pm *Finish*

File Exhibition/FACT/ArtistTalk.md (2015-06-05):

##Artist Talk for FACT

###Structure
### What is DoESLiverpool?

Its a makerspace: it's related to the FACT lab and other cultural 'labs' for collaboration and production refer to I think

* A community of people and Community Interest Company with diverse skills and interests. Any profit helps the community.
* A co-working space in the heart of Liverpool with desks available to rent. 
* We host and organise events.
* A workshop with 3Dprinters & lasercutters.
* A place where you do your best work, to support the growth of the region in a meaningful way – by doing.
* A friendly environment fostering collaboration.
* Get involved!
* http://doesliverpool.com/get-involved/

###Notes

 * Anything online is global
 * Interactivity? Collaboration
 * Makerspaces let you Build Your Own
 * Laser etched signs
 * Vinyl Cutter
 * Build our own workflow tools
 * Somebody-should
 * Loose Ties

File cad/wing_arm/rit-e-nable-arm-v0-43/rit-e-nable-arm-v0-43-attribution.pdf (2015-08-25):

# RIT e-NABLE Arm v0.43

## By e-NABLE

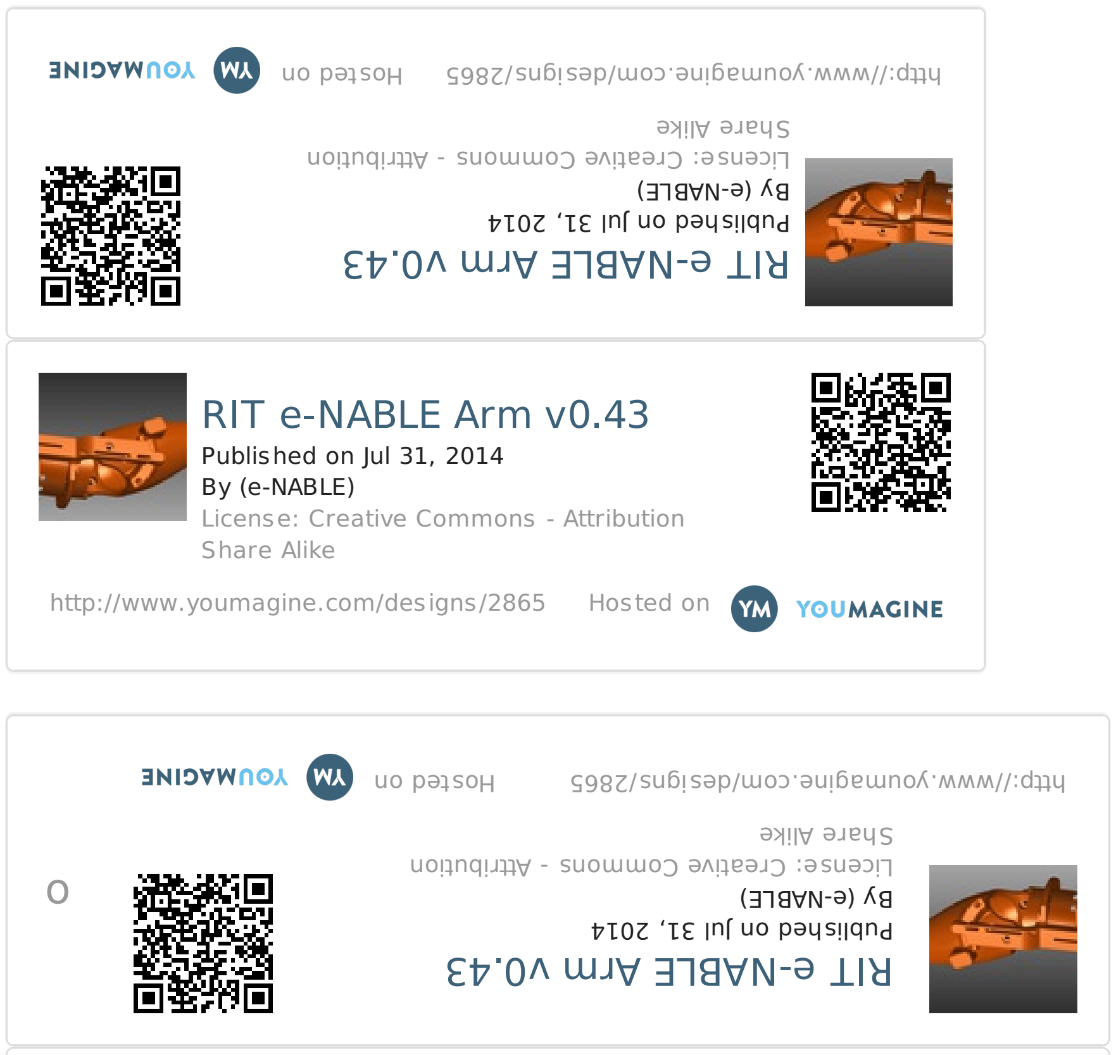
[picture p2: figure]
RIT e-NABLE Arm v0.43; Published on Jul 31, 2014 By (e-NABLE) License: Creative Commons - Attribution Share Alike; http://www.youmagine.com/designs/2865; Hosted on

o

## RIT e-NABLE Arm v0.43

Published on Jul 31, 2014
By (e-NABLE)
License: Creative Commons - Attribution Share Alike

http://www.youmagine.com/designs/2865 Hosted on

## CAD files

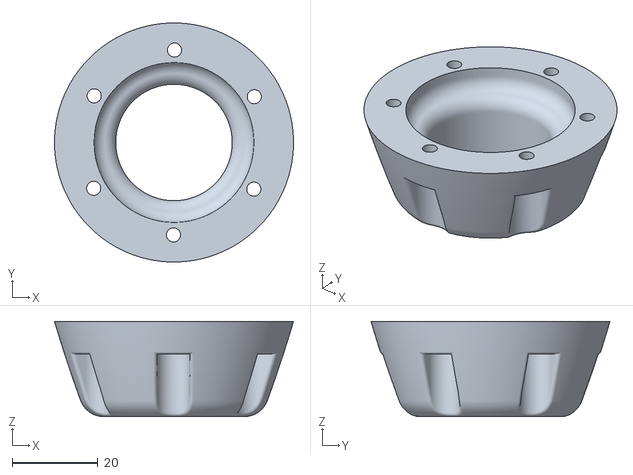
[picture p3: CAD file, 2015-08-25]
cad/wing_arm/rit-e-nable-arm-v0-43/cup_assembly_Retainer_2.stl
55.8 x 55.8 x 22.2

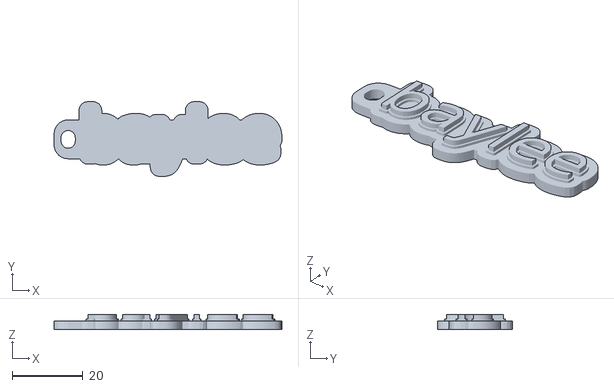
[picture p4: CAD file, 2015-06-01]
cad/hands/baylee/0-prerequisites/baylee.stl
64.3 x 21.1 x 4.20

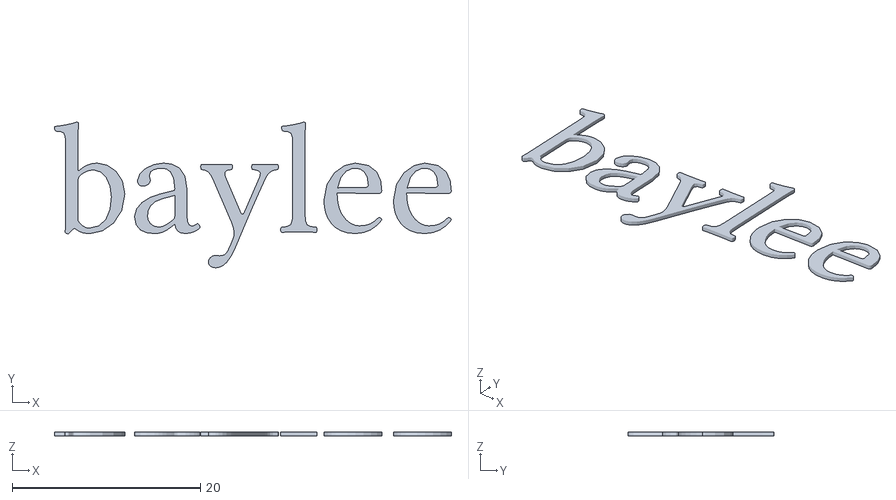
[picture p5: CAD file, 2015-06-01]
cad/hands/baylee/1-fingers/baylee.stl
42.2 x 15.5 x 0.4

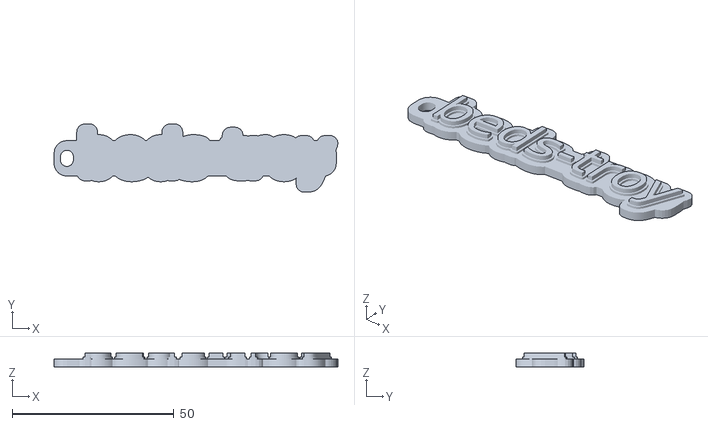
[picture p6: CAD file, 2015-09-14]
cad/hands/beds-troy/0-prerequisites/Purple-0-beds-troy.stl
87.9 x 21.1 x 4.20

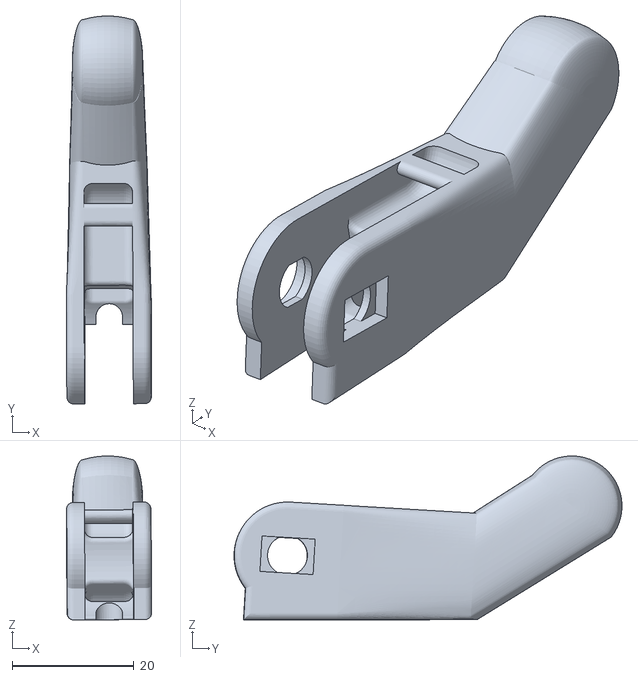
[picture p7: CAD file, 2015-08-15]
cad/hands/beds-troy/1-fingers/raptor_2.0_fingertip-3.stl
14.0 x 63.8 x 27.0

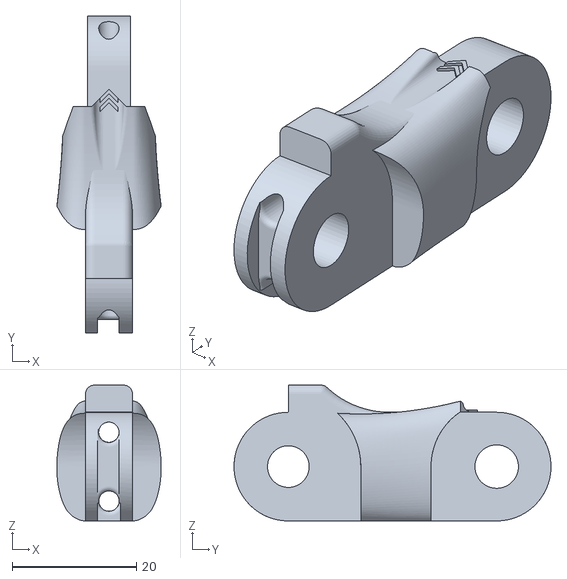
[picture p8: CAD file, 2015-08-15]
cad/hands/beds-troy/2-proximal/raptor_2.0_proximal-2.stl
16.8 x 51.1 x 21.9

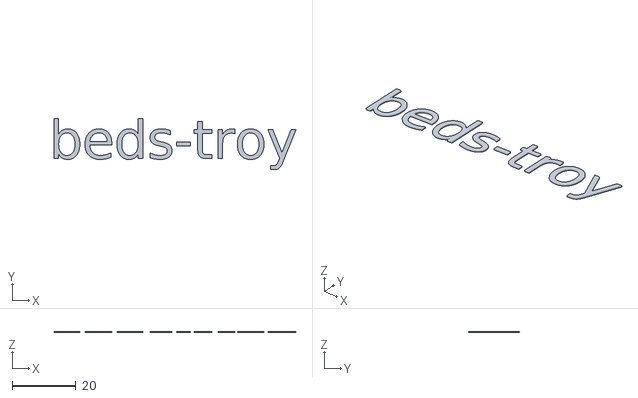
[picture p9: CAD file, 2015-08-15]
cad/hands/beds-troy/3-gauntlet/Silver-3-beds-troy.stl
75.9 x 16.1 x 0.4

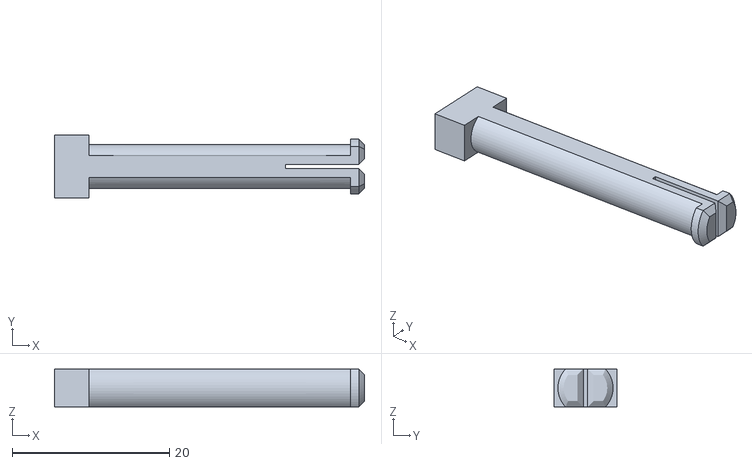
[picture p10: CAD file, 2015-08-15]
cad/hands/beds-troy/4-palm/raptor_reloaded_knuckle_pin-2.stl
39.4 x 8.03 x 4.82

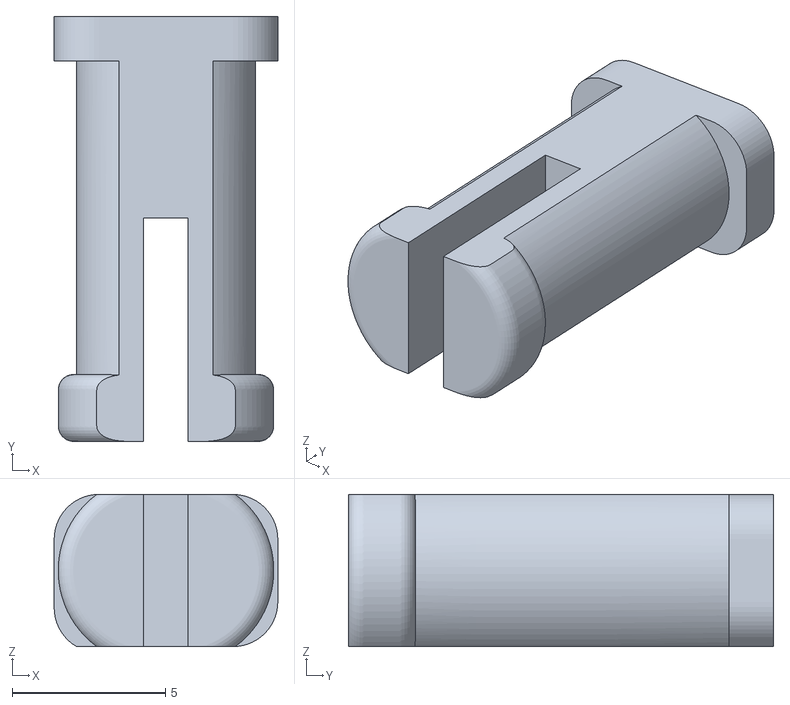
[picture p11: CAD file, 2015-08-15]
cad/hands/beds-troy/5-tensioner/raptor_2.0_finger_pin-2.stl
7.30 x 13.9 x 4.97

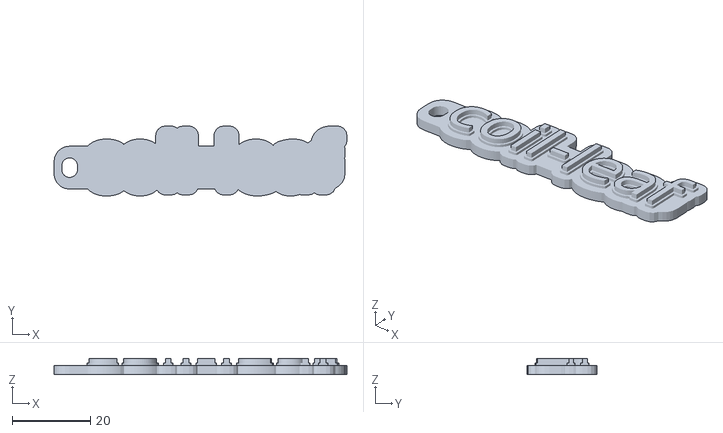
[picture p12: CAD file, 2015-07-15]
cad/hands/coil-leaf/0-prerequisites/blue-0-coil-leaf.stl
75.0 x 17.9 x 4.20

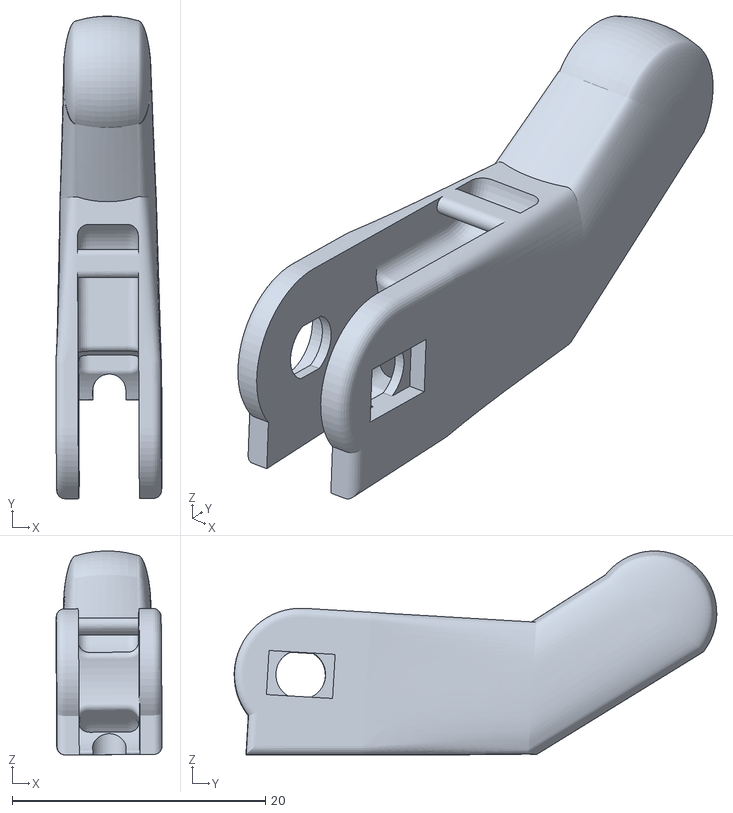
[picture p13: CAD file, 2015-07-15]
cad/hands/coil-leaf/1-fingers/raptor_2.0_fingertip-4.stl
8.39 x 38.1 x 16.1

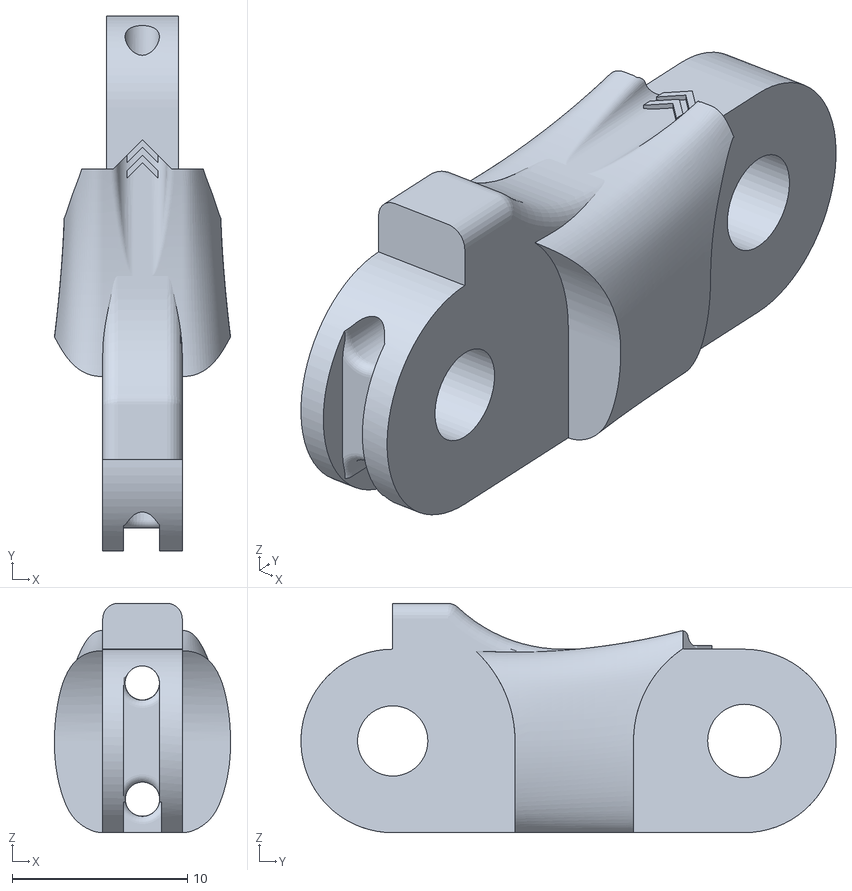
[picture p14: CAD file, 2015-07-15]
cad/hands/coil-leaf/2-proximal/raptor_2.0_proximal-4.stl
10.1 x 30.5 x 13.1

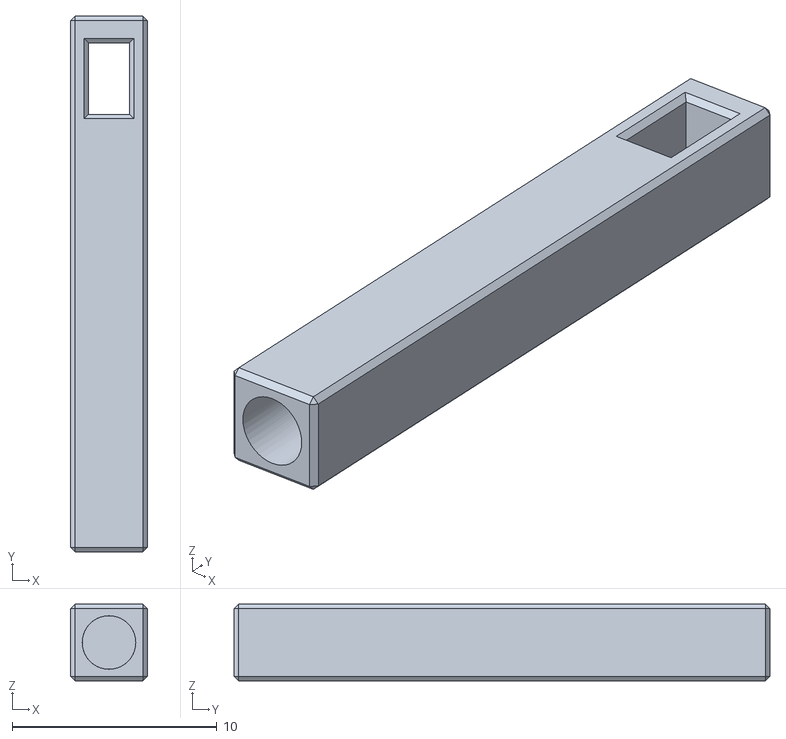
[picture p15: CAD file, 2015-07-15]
cad/hands/coil-leaf/3-gauntlet/raptor_reloaded_tensioner_pin-4.stl
3.75 x 26.2 x 3.75

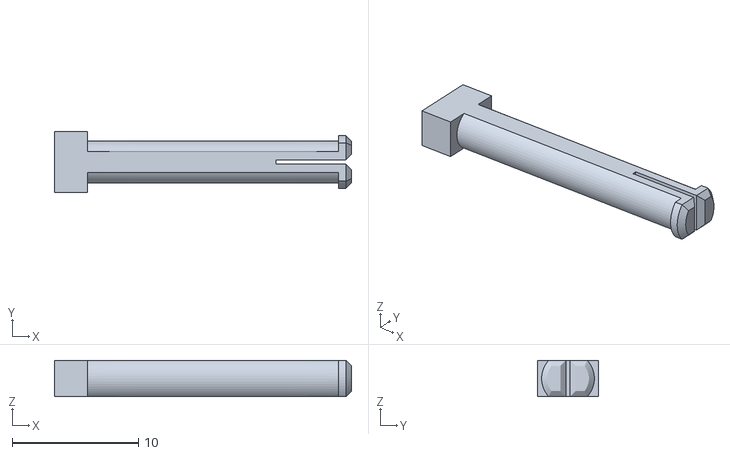
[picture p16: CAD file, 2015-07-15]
cad/hands/coil-leaf/4-palm/raptor_reloaded_knuckle_pin-2.stl
23.6 x 4.80 x 2.88

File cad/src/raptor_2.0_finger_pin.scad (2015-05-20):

include <scaling.scad>;

scale([SCALE,SCALE,SCALE])
    import("raptor_2.0_finger_pin.stl");

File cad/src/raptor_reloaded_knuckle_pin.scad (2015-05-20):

include <scaling.scad>;

scale([SCALE,SCALE,SCALE])
    import("raptor_reloaded_knuckle_pin.stl");

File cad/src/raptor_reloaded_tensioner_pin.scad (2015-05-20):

include <scaling.scad>;

scale([SCALE,SCALE,SCALE])
    import("raptor_reloaded_tensioner_pin.stl");

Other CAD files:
cad/src/raptor_reloaded_thumb_pin.scad
cad/TestToolPaths/DoESLigoMinecraft.stl
cad/hands/Mars-teeth/0-prerequisites/hook-long-1.stl
cad/hands/Mars-teeth/0-prerequisites/hook-long-2.stl
cad/hands/Mars-teeth/0-prerequisites/hook-long-3.stl
cad/hands/Mars-teeth/0-prerequisites/hook-long-4.stl
cad/hands/Mars-teeth/0-prerequisites/hook-long-5.stl
cad/hands/Mars-teeth/0-prerequisites/hook-long.stl
cad/hands/Mars-teeth/0-prerequisites/yellow-0-Mars-teeth.stl
cad/hands/Mars-teeth/1-fingers/raptor_2.0_fingertip-1.stl
cad/hands/Mars-teeth/1-fingers/raptor_2.0_fingertip-2.stl
cad/hands/Mars-teeth/1-fingers/raptor_2.0_fingertip-3.stl
cad/hands/Mars-teeth/1-fingers/raptor_2.0_fingertip-4.stl
cad/hands/Mars-teeth/1-fingers/raptor_2.0_fingertip-5.stl
cad/hands/Mars-teeth/1-fingers/raptor_reloaded_wrist_pin_cap-1.stl
cad/hands/Mars-teeth/1-fingers/tag-1.stl
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

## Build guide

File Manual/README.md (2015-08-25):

##Print & Assembly Manual

**Manual for Gallery Guides manning the DesktopProsthetics Project as part of the FACT/Crafts Council show Build Your Own**
* [ ] Manual complete

###Printing

On **Saturday 6th June 2015** on the [Measuring workshop](https://github.com/cheapjack/buildyourown/blob/master/events/MeasuringUpWorkshop.md) we will have generated all the files required for printing over the course of the exhibition.

As gallery guide you are essentially supporting the fulfilment of these 'orders' in a print queue. Each participant is measured, given a code and some colour choices recorded (pink, red, blue, green, white or silver)

Name | CodeName | Measurement | PalmGauntlet Colour | Extremity Colour
------------ | ------------- |------------ | ------------- |------------
Baylee Abbott | Baylee | 63mm | Pink | Blue
Adult Demo Hand | Demo-85 | 85mm | Red | Silver

This info is inputted into a programme that generates **.stl** print files seperated into **'build plates'** i.e. a plate of finger prints, a plate for palms etc and uploaded by DoESLiverpool onto SD cards in the printers. Gallery Guides are not involved in this process

 * 0-prerequisites
 * 1-fingers
 * 2-proximal
 * 3-gauntlet
 * 4-palm
 * 5-tensioner

The file generation system DoES uses also adds the colour to each plate file name and you can refer to the [Print Queue](https://github.com/cheapjack/buildyourown/blob/master/Manual/PrintQueue.md) document to cross reference colour and other details.

All the files will be loaded onto the printers and can be selected for printing using the rotary selector on the Ultimaker2. Please refer to the Gallery Copy Manual for setting up and starting printing.

Each hand has a 0-prerequisites build plate which once printed on the printer include 2 name tags featuring the code/username of the participant, one for them to keep as a key ring and one to hook onto a wall mounted clear plastic storage box. It also prints the 6 hooks required to hook this onto the boxes. Once the username tag is placed hooked onto the container, this container will hold all the hand parts for this particular hand and is permanently associated to that participant. More boxes will be made available.

Each subsequent plate prints a 2 layer text of the username for reference plus a plate number tag for hooking onto (not for hooking onto the box, we've done that in pre-requisites)

You work through printing each plate; once a plate is complete it's contents are removed from the print plate (see manual, increasing the bed temperature to 36 degrees helps remover the items easily) and placed in the correct clear plastic box; it will be labelled from the pre-requisite step. You dont have to do each plate in order; if there is red PLA preloaded it makes sense to do a red build plate; cycle through the menu and select a file to print, referrring to the wall boxes to check it has not already been printed.

Only select files that have the correct colour loaded onto the Ultimaker; look at the material at the back to see the colour currently loaded. If you choose a colour different to one already loaded please follow the Ultimaker manual guideline to change the PLA material

All print stock is PLA and the Ultimaker 2 should be set to print this at all times.

Most days a print will be already running and you only have to watch for failed prints

###Print Fails

If a print fails, pause and then abort the print. Take off everything from the bed and place in a box marked fail with a note of the name and plate number. Re-prepare the plate check it is not overloaded with pritt stick and restart the file; then onc the corrected component is printed, say 1 finger needs a re-print, let it start the next print then pause and abort and check youve completed that plate.

If the print continues to fail, refer to the troubleshooting section of the Ultimaker Manual but its usually:
 * The pritt stick has built up too thick and the plate needs removing,  a wash in warm soapy water and thorough dry
 * The plate is no longer level and needs a reset

Refer to additional Troubleshooting [here](https://github.com/cheapjack/buildyourown/blob/master/Manual/Troubleshooting.md)

If you cannot troubleshoot contact DoESLiverpool, Ross, Patrick or Adrian and they will try talk through the problem and failing that come in to troubleshoot direct

###Assembly Manual

Refer to Video for Raptor hand original design and then follow more detailed information for the Raptor-Reloaded hand DesktopProsthetics is using below.

<a href="http://www.youtube.com/watch?feature=player_embedded&v=5HVwC3RnWXk
" target="_blank">IMAGE ALT TEXT HERE</a>

parts

*Clean and prep all parts*
 * 1 x Raptor Palm
 * 1 x Gauntlet
 * 1 x Tensioner
 * 1 x Retention_clip
 * 1 x Thumb Pin
 * 2 x Wrist Pins
 * 5 x Finger Pins
 * 2 x Knuckle Pins
 * 5 x Proximals
 * 5 x Fingertips
 * 2 x Wrist Caps
 * Nylon cord
 * Elastic
 * Tensioner pins

 * Connect Proximals with Fingertips



 * Give all the surfaces that move against another part a light sanding down with sandpaper so that they move freely 
 * Connect them first without pin and ensure they are cleaned sufficiently to move loosely
 * Prep elastic size, with enough length to run over end of palm. 
 * Melt ends with lighter to prevent fraying
 * Knot one end 
 * Thread into the fingertip and loop back through to go through the proximal




 * Insert finger pin, round 'snap' pin first





 * Connect proximals to palm using knuckle pins, tap them in gently with a hammer
 * Connect thumb proximal to thumb joint on palm with thumb
 * Connect gauntlet to palm using the 2 wrist pins
 * Feed the unknotted end of the elastic into the passage in the knuckles loop and loop back and tie securely



 * Feed all the way through the palm channel, loop over and knot to provide quite a strong tension
 * Connect the Palm with Gauntlet using the wrist pins and caps



 * Now assemble the Retention clip and tensioner with pins and non-elastic cord this will engage the grip and needs some adjustment
 * Tie off the non-elastic cord to the underneath tie off point of the fingers. This cord will share the top palm channels that the elastic and non-elastic cords feed through, a channel for each finger and thumb.
 * Thread the non-elastic cord from the underneath of the fingers (from the underneath tie off) and through and under the proximals, through and under the knuckle hole and then fed over the palm through the palm cord channel alongside the elastic.
 * If you feed it right the non-elastic cord will feed under the elastic which is tied off at the base of the palm over the top of the palm bridge and be tied to a tensioner pin.
 * Remember Each cord is fed through the underneath of the fingers and knotted securely to the underneath tie off point of the finger
 * tie off the end of the non-elastic to the square hole in the end of the tensioner pin.
 * Each tensioner is inserted into the tensioner clip and tensioner and a 3M screw screws into the base of the pin from the rear of the tensioner to secure in place and allow adjustment.
 * For those of you without a working wrist there is some adjustment to the non-elastics to make it fit the Raptor wing which we have a prototype for at the Assembly workshop

*Steps incomplete needs work*



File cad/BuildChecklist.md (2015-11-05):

##BuildChecklist

#### Exhibition closed, Liverpool print queue complete, wings in progress at DoES does Prosthetic Interest group.
#### Refer to [issue #85](https://github.com/cheapjack/buildyourown/issues/85)

Checklist for Raptor-Reloaded print progress at DesktopProsthetics in FACT **(now closed)**

BuildName | All Plates Printed | Assembled | Fitted | Collected | Requires Reprint (new codename)
------------ | ------------- |------------ | ------------- | ------------ | -------------  
gasp-law | <ul><li>[x] </li>| <ul><li>[ ] </li>| <ul><li>[ ] </li>| <ul><li>[x] </li>| <ul><li>[ ] </li>
gin-timers | <ul><li>[x] </li>| <ul><li>[x] </li>| <ul><li>[ ] </li>| <ul><li>[x] </li>| <ul><li>[ ] </li>
guts-squid | <ul><li>[x] </li>| <ul><li>[ ] </li>| <ul><li>[ ] </li>| <ul><li>[x] </li>| <ul><li>[ ] coil-Mars</li>
leaf-keeps | <ul><li>[x] </li>| <ul><li>[x] </li>| <ul><li>[ ] </li>| <ul><li>[x] </li>| <ul><li>[ ] eddy-troops</li>
gushes-eddy | <ul><li>[x] </li>| <ul><li>[ ] </li>| <ul><li>[ ] </li>| <ul><li>[x] </li>| <ul><li>[x] beds-troy</li>
manual-guts | <ul><li>[x] </li>| <ul><li>[ ] </li>| <ul><li>[ ] </li>| <ul><li>[x] </li>| <ul><li>[ ] </li>
Mars-teeth | <ul><li>[x] </li>| <ul><li>[ ] </li>| <ul><li>[ ] </li>| <ul><li>[x] </li>| <ul><li>[x] tuck-guts</li>
coil-leaf | <ul><li>[x] </li>| <ul><li>[ ] </li>| <ul><li>[ ] </li>| <ul><li>[x] </li>| <ul><li>[ ] peewee-undies</li>
trite-keeps | <ul><li>[x] </li>| <ul><li>[ ] </li>| <ul><li>[ ] </li>| <ul><li>[x] </li>| <ul><li>[x] gin-trite</li>
month-reared | <ul><li>[x] </li>| <ul><li>[ ] </li>| <ul><li>[ ] </li>| <ul><li>[x] </li>| <ul><li>[ ] </li>

### DoES Liverpool Print Queue

Hands still being printed at DoES Liverpool now exhibition ended passed on to interest group

BuildName | All Plates Printed | Assembled | Fitted | Collected | Requires Reprint 
------------ | ------------- |------------ | ------------- | ------------ | ------------- 
beds-troy | <ul><li>[x] </li>| <ul><li>[ ] </li>| <ul><li>[ ] </li>| <ul><li>[ ] </li>| <ul><li>[ ] </li>
coil-Mars | <ul><li>[x] </li>| <ul><li>[ ] </li>| <ul><li>[ ] </li>| <ul><li>[ ] </li>| <ul><li>[ ] </li>
eddy-troops | <ul><li>[x] </li>| <ul><li>[ ] </li>| <ul><li>[ ] </li>| <ul><li>[ ] </li>| <ul><li>[ ] </li>
gin-trite | <ul><li>[x] </li>| <ul><li>[ ] </li>| <ul><li>[ ] </li>| <ul><li>[ ] </li>| <ul><li>[ ] </li>
grows-abort | <ul><li>[x] </li>| <ul><li>[ ] </li>| <ul><li>[ ] </li>| <ul><li>[ ] </li>| <ul><li>[ ] </li>
ruing-beds | <ul><li>[x] </li>| <ul><li>[ ] </li>| <ul><li>[ ] </li>| <ul><li>[ ] </li>| <ul><li>[ ] </li>
peewee-undies | <ul><li>[x] </li>| <ul><li>[ ] </li>| <ul><li>[ ] </li>| <ul><li>[ ] </li>| <ul><li>[ ] </li>
tuck-choosy | <ul><li>[x] </li>| <ul><li>[ ] </li>| <ul><li>[ ] </li>| <ul><li>[ ] </li>| <ul><li>[ ] </li>
tuck-guts | <ul><li>[x] </li>| <ul><li>[ ] </li>| <ul><li>[ ] </li>| <ul><li>[ ] </li>| <ul><li>[ ] </li>
undies-manual | <ul><li>[x] </li>| <ul><li>[ ] </li>| <ul><li>[ ] </li>| <ul><li>[ ] </li>| <ul><li>[ ] </li>
code-name | <ul><li>[x] </li>| <ul><li>[ ] </li>| <ul><li>[ ] </li>| <ul><li>[ ] </li>| <ul><li>[ ] </li>

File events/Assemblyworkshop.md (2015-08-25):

## Assembly Workshop


Image source [Enabling the Future on Thingiverse](http://www.thingiverse.com/thing:476403) Licensed under [Attribution-ShareAlike 3.0 Unported (CC BY-SA 3.0)](http://creativecommons.org/licenses/by-sa/3.0/ "License Link")
### **Saturday 8th August** & **Saturday 22nd August** FACT Gallery 1 12pm-4.30pm FREE

[FACT Listing and Booking Link](http://fact.co.uk/whats-on/current/does-assembling-workshop)

**Age 3 and above, children accompanied by an adult**
### DoESLiverpool will be helping Finish, Assemble, test and fit printed hands from the DesktopProsthetics Project

 * [x] Copy signed off

## Workshop activity
* Re-Introduction to project 
* Learning how to assemble a raptor
* Test and fit hands
* Log any issues and improvements required for the hands
* Point to DoES does Prosthetics Day

### Session Plan
 * 12pm **Introduction by Jason Abbott, Baylee Abbott, @amcewen @cheapjack @defproc**
 * 12.20pm **Notes on Health & Safety from Ross and Drew**
 * 12.30pm **Start assembling with Patrick, Adrian, Ross, Baylee and Jason**
 * *Measuring work flow*
   * Refer to youtube video using screen
   * Input into System & record

code-name | Printed? | Assembly complete | Issues | Issue detail |
------------ | ------------- |------------ | ------------- |------------ |
gasp-law | <ul><li>[x] </li>| <ul><li>[ ] </li>| <ul><li>[ ] </li>| <input type="text" id="issue" name="issue"/></input> |
gin-timers | <ul><li>[x] </li>| <ul><li>[ ] </li>| <ul><li>[ ] </li>| <input type="text" id="issue" name="issue"/></input> |
guts-squid | <ul><li>[x] </li>| <ul><li>[ ] </li>| <ul><li>[ ] </li>| <input type="text" id="issue" name="issue"/></input> |
leaf-keeps | <ul><li>[x] </li>| <ul><li>[ ] </li>| <ul><li>[ ] </li>| <input type="text" id="issue" name="issue"/></input> |
gushes-eddy | <ul><li>[x] </li>| <ul><li>[ ] </li>| <ul><li>[ ] </li>| <input type="text" id="issue" name="issue"/></input> |
manual-guts | <ul><li>[x] </li>| <ul><li>[ ] </li>| <ul><li>[ ] </li>| <input type="text" id="issue" name="issue"/></input> |
ruing-beds | <ul><li>[ ] </li>| <ul><li>[ ] </li>| <ul><li>[ ] </li>| <input type="text" id="issue" name="issue"/></input> |
Mars-teeth | <ul><li>[ ] </li>| <ul><li>[ ] </li>| <ul><li>[ ] </li>| <input type="text" id="issue" name="issue"/></input> |

## Equipment List

* Calipers 
* Cabling laptop to HDMI
* Elastic
* Pins and screws
* fine sandpaper
* Superglue
* Junior hacksaw
* Scissors
* A needle
* Screwdrivers
* Pliers
* Tweezers
* Cigarette lighter

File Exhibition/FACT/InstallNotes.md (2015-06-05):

##Install Notes

###Install printers Wednesday 3rd June 2015

*List of items to bring into FACT*

 * [x] Printed hands sets
 * [x] Hand Parts
 * [x] Ultimaker Printers x 2
 * [x] Printer consumables
 * [x] Power Supplies, Boxes, Manuals and Ephemera
 * [x] Calipers from DoES
 * [ ] Tweezers
 * [ ] Stanley Knife
 * [ ] Cigarette Safety Lighter for elastic fraying
 * [x] Scalpel
 * [x] Scalpel blades
 * [x] Safety Glasses
 * [ ] Replacements for tensioner threaded pins need wider head or washers
 * [ ] New Self tapping screws for velcro
 * [x] Cutting mat
 * [x] Vitrine vinyl
 * [x] DoES Business cards and stickers
 * [ ] Some kind of workflow Manual for Gallery Guides
 * [x] Application tape and squeedgy for vinyl
 * [x] Cut vinyl for sub plinths
 * [x] Vitrines (in FACT)
 * [x] Part Storage
 * [ ] Print for e-NABLE Health & Safety handouts and Liability forms
 * [x] Tablet/ipad whatever to display complete stl model in browser something like [Jscad](http://openjscad.org/)
 * [x] Supported by Ultimaker sign
 * [ ] Spare SD cards for transferring models
 * [x] [Thwack](http://www.thingiverse.com/thing:34404) 3D printed mallet x 2

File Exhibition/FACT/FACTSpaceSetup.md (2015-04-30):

###FACT Space Setup

> _**Outstanding questions formatted like this**_

Current preferred setup as of 28/4/15

*Option 3*
byo does story option 3b
byo latest 28_04 does printbench

> _**Needs commenting and confirming in issue #12**_
* [ ] Confirm setup

*Original suggested setup*
byopsetup

pegboard

* On 4 Wall mounted shelves in a ‘run’: 2 x Ultimaker Printers, all fully perforated pegboard sheetshttps://ultimaker.com/en/products/ultimaker-2-family The ultimakers footprint is W 338 x D 358 x H 289 mm so dont know if we can use your standard shelf to support that; may need them a bit deeper and with extra support for safety, not sure on weight. We thought we have a setup as above but with an extra panel on the right, with the 3 printers spaced out on the shelves but with complete peg board panels behind for displaying/storing printed components; maybe one of the four could be hit and miss panels for any warning/info signs. Run power up the back of the panels

* The peg board around the printers will hold a number of clear storage bins - 8-12 larger ones (such as the [Storbox Big](http://www.shopfittings4u.co.uk/product_group.asp?parseid=85&i=116)) to hold spare printer filament, and around 15 smaller ones (such as the [Storbox Cube](http://www.shopfittings4u.co.uk/product_group.asp?parseid=84&i=116)) to store tools and the printed hand parts.

vitrine

### "5 steps to a new hand"
On wall mounted shelves, possibly with clear vitrine with mix of hit and miss panels for displaying info

**5 'plinths' essentially**

1. Measuring & Model
  * Measuring hands and using the Enabling The Futures [Handomatic](http://webapp.e-nable.me/ "Link to the Handomatic Web App") Web Application
  * Exhibits:
    * A set of calipers for measuring
    * A tablet (provided by FACT) running the Handomatic app to show the digital model

> _**Q: [Do we need to secure the calipers?](https://github.com/cheapjack/buildyourown/issues/18)**_

2. Print
  * Print instruction diagram plus a set of straight-off-the-3d-printer printed parts
  * Exhibits, in a vitrine:
    * A full set of straight-off-the-3d-printer printed parts

3. Tidy parts
  * Use tools from the toolbench to help clear/clean and prep components for assembly
  * Exhibits, in a vitrine:
    * A set of parts with support material, etc. removed
    * A hand-drill
    * A Stanley knife
    * A scalpel
    * A cutting mat
    * A collection of bits of support material

4. Collect Things
  * All the parts you'll need to assemble your hand
  * Exhibits, in a vitrine:
    * A set of cleaned up parts
    * Nuts and bolts
    * Cords, etc.

5. Assembly
  * A finished hand
  * Exhibits, in a vitrine:
    * A fully-assembled, finished hand

tablewithwheelchair

* Another table or multi-accessible workbench with space for assembly and prepping of components
  * all the things you can play with. 
  * Up printer possibly on here
  * Toolbench
    * We need tools to help prep the components possibly making dowels for sanding components down
    * Gloves and safety glasses and pliers, could be stored on the pegboards behind the printer 'plinths'/shelves
  * This is the space for assembly/workshopping. 
  * Power
  * Wheelchair accessible as image above:
  * Mix of benches and individual stools?

* Print Queue server management using [OctoPrint](http://octoprint.org/ "Octoprint website") print queue system run off pi or tablet, potentially So there may be a way of alerting the person whose pieces are being printed

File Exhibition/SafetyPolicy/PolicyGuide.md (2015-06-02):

###e-NABLE Policy Reminder by
###e-NABLE Support and Matcher Teams

First, thank you!  e-NABLE would be impossible without our amazing volunteers who donate their time, talents, filament and printer time to create prosthetic  these hands for people all over the world.

Second, please remember that our our collective success and reputation rests on your shoulders.  
Please make sure you abide by our policies.

1).  Make sure you have filled out our intake form at http://goo.gl/lW1uX6.  We can not match you with anyone until this information is received. 

2.)  If you have been matched by someone local to you, please refrain from having recipients in your home or visiting them at their residence. We know everyone is here to help, and that residential meetings may be more convenient and personal, but it is crucial that we avoid the complicated and potentially negative situation that could result. 

Some recommended locations for meeting with recipients and their families:
• Local Library
• Mall food courts
• Local park with picnic tables (for tools etc if needed)
• Local restaurants (kid friendly if you are meeting with a family!)
• Some science museums have open areas/Food courts etc

3.)  We sometimes work with under-age recipients who proactively find their own way to us.  This is admirable, but parental permission is required and correspondence should be overseen by the parent/guardian. If you notice a post in the community by a potential recipient who appears to be under the age of 18, please tag Jen Owen or Melina Brown in the comments.  

Abiding by these simple policies...religiously!... keeps our recipients and our organization safe.  

When you abide by these simple policies, you are enabling the future we all want.
If you deviate from them, you put us all in jeopardy.

If you have questions about your own practices, or about those of another e-NABLE volunteer, please email enablematcher@gmail.com or jschull@enablecommunityfoundation.org

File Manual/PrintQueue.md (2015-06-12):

## Print Queue

Measurements and details of participants in the **DesktopProsthetics** project for Gallery Guide reference
*NB Contact Detail not held on github*

No. | Name | CodeName | Measurement | Palm Colour | Extremity Colour | Contact Detail 
---------- | ------------ | ------------- |------------ | ------------- |------------ |------------
0 | Baylee Abbott | Baylee | 63mm | Pink | Blue |
0 | Adult Demo Hand | Demo-85 | 85mm | Red | Silver |
1|        |        |        |        |        
2|        |        |        |        |       
3|        |        |        |        |        
4|        |        |        |        |        
5|        |        |        |        |        
6|        |        |        |        |        
7|        |        |        |        |        
8|        |        |        |        |        
9|        |        |        |        |        
10|        |        |        |        |        
11|        |        |        |        |        
12|        |        |        |        |        
13|        |        |        |        |        
14|        |        |        |        |        
15|        |        |        |        |        
16|        |        |        |        |        
17|        |        |        |        |        
18|        |        |        |        |        
19|        |        |        |        |        
20|        |        |        |        |

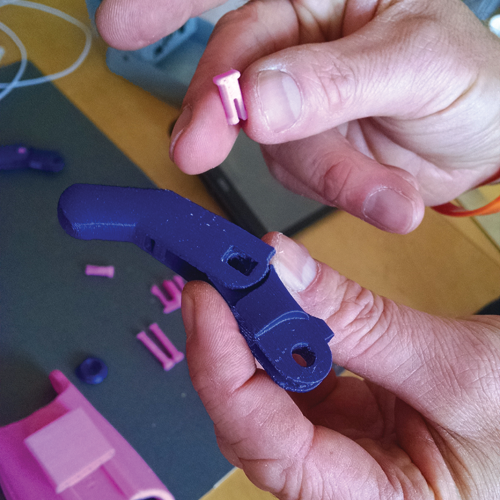
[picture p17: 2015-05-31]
Manual/ManualImages/1.png

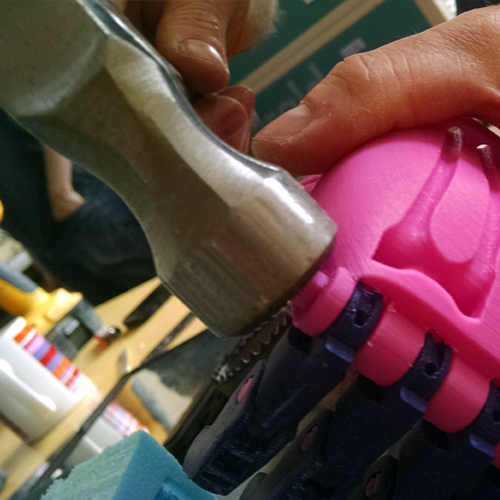
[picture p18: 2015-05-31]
Manual/ManualImages/7.png

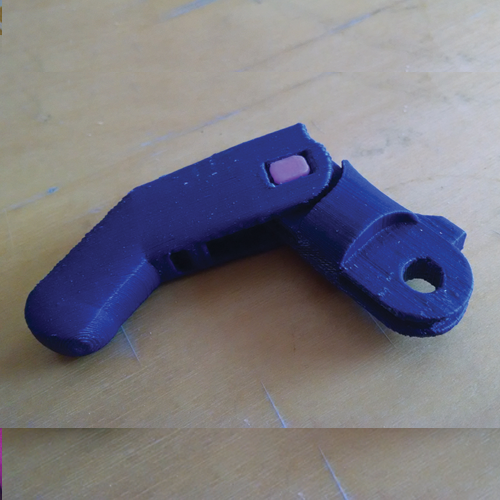
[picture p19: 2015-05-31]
Manual/ManualImages/2.png

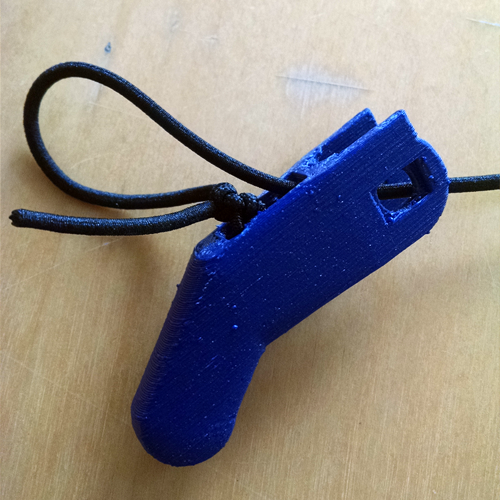
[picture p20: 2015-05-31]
Manual/ManualImages/4.png

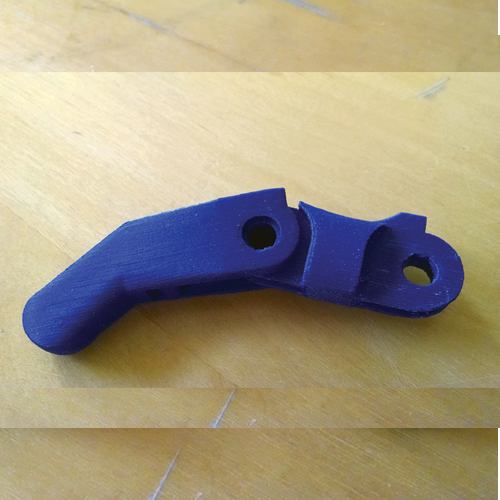
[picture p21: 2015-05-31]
Manual/ManualImages/3.png

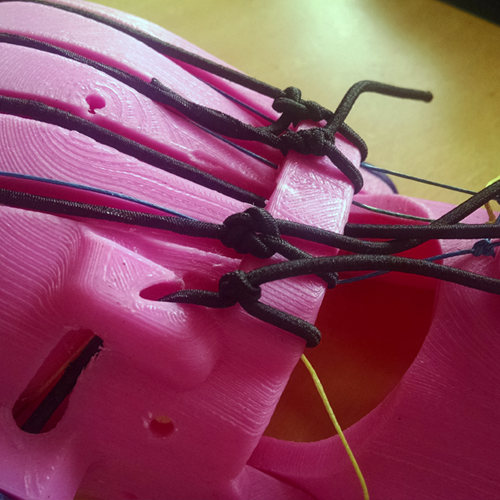
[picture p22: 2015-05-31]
Manual/ManualImages/8.png

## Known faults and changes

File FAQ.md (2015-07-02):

# Desktop Prosthetics - Frequently Asked Questions

This page provides answers to some of the more frequently asked questions about the Desktop Prosthetics project.  See the [Background](Background.md) page for more general information about the exhibition and people involved.

[Enabling the Future](http://enablingthefuture.org/), the global project whose designs we'll be using for the prosthetics have [an extensive FAQ](http://enablingthefuture.org/faqs/media-faq/) which is worth reading through in addition to this one.

### How long does the actual process of printing a hand take?

As each hand is custom to its recipient - varying a bit in size, but also customised based on the person's needs, with/without a thumb, etc. - there's no exact answer.  However,

Taking one of the hands we've printed as an example, there are 14 parts in total:

 * Gauntlet - 10 h 39 m, 69.7g of plastic
 * Palm - 16 h 45 m, 96.2g of plastic
 * Fingers - 13 h 53 m, 79.8g of plastic
 * Other parts - 5 h 13 m, 30.5g of plastic
 * Hinge caps - 0 h 26 m, 2.8g of plastic

So in total that's 47 hours of printing and 280g of plastic.  The weight includes the support material used during the printing, which is removed later, but when you add the metal hinge pins and cords, the resultant weight will probably be similar.

### What materials are used?

The particular plastics used will depend on the 3d printer and what materials it can print.  Generally it will be either ABS (the same plastic Lego is made from) or PLA (a plant-based thermoplastic which has similar properties to ABS).  Enabling the Future recommend printing in PLA, so we'll be using that for the hands we print in the exhibition.

In addition to the plastic parts there are a number of metal screws and nuts, some elastic and cord, foam padding, velcro, etc. used to hold the parts together and attach them to the user's arm.

### What operations are possible with these prosthetics?

See the "Q: What can these 3D printed hands be used for?" question in the [Enabling the Future Media FAQ](http://enablingthefuture.org/faqs/media-faq/)

### Is it safe?

*e-NABLE Device Safety Guidelines Statement*

"Based on preliminary testing and observations on the functionality and capabilities of our experimental 3D printed prosthetic devices it is felt that they are currently not safe for operation of heavy machinery, tools, equipment, and vehicles due to low grip strength development. These prosthetic devices have shown, however, to provide some functionality for gross grasp activities of light and pliable objects, but it is in no way a substitute for a fully functioning hand. In addition, we don’t recommend the use of our experimental 3D printed prosthetic devices for small children (i.e., under 3 years of age) due to greater fall rate and the need of sensory input through oral stimulation. Furthermore, it is unknown if our experimental 3D printed prosthetic devices are able to sustain a small child’s bite without breaking. Please review and consider the following recommendations and precautions regarding the 3D printed prosthetic device"

By taking part in this project and using a hand you agree to follow the [detailed Safety Guidelines here](http://enablingthefuture.org/build-a-hand/safety-guidelines/)

### Who will be helped through this project?

By working with [Reach](http://reach.org.uk/), the association for children with upper limb deficiency, we'll be helping a number of children (primarily) from the North-West and East Anglia.  In addition, the exhibition will raise awareness within the Reach community and the general public about some of the more practical uses for 3d printing.

The main limit to who could get a hand comes from the size of prints we can produce on these particular 3D printers.  It should work for hands up to 120mm across the knuckles, which will cover most adult hand sizes too.

For this project, we're focusing on the Raptor Reloaded design.  This requires the user to have a wrist in order for it to fit properly.  The wider Enabling the Future project has a [greater selection of designs to cater for other needs](http://enablingthefuture.org/upper-limb-prosthetics/).

### Is this a project DoES Liverpool is looking to expand?

DoESLiverpool like many makerspaces and hackspaces, as an organisation do not do projects in a sense, we simply help our community to realise their projects with the facilities we have. Our community is essentially anyone who wants to do something with us. 

This collaboration with FACT was inspired from a local family printing a prosthetic hand in our workshop and the 3 members of the community leading the project have interests and skills in 3D printing.

Part of the deal of this project is that DoESLiverpool and Norwich Hackspace can keep the new larger 3D printers so that if people do need to print more hands in the future, we will have extended our facilities so that they can.  

If a group grows and develops around the activity in the exhibition then that group can continue to   use DoESLiverpool to support it like the many diverse groups that call DoESLiverpool home.

### What if the measuring Workshops are full and I can't get a hand printed in the exhibition period?

**DesktopProsthetics** is a project with FACT within an exhibition: and like other things you can make at DoESLiverpool it's not a service and it can be hard to sustain and help everyone interested in a hand, so we cannot guarantee we can print a hand for the people who need them. 

But we can help point people in the right direction and help them **do it themselves** which is what the project is about. However we'd love to see a community grow around this project but it will take new people to drive it. DoES Liverpool do have regular **Maker Nights** and **Maker Days** where people can learn more about DoES facilities, meet other people and this is a good start. We won't be taking details of people who have not been able to take part in the exhibition but we are having a **DoES does Prosthetics Day** at DoES Liverpool **Saturday 15th August 2015** Details to follow. This is particularly about printing prosthetics and how people can get involved in e-NABLE and an interest group in Liverpool, so join the [DoES Liverpool Google Group](http://doesliverpool.com/get-involved/) to stay informed. 

We've a list of further ways of getting involved if you have not been able to be measured at the measuring workshop and print a hand.

* Visit the exhibition at FACT **4th June - 31st August 2015 at [FACT](http://fact.co.uk/projects/build-your-own-tools-for-sharing.aspx?when=futureevents)**
**Gallery 1, FACT, 88 Wood Street, Liverpool, L1 4DQ**
* Join the community **meetup** at a **DoES does Prosthetics Day** at DoES Liverpool **Saturday 15th August 2015** Details to follow
* Look out for **Maker Nights** and **Maker Days** on the [DoESLiverpool Calendar](http://doesliverpool.com/calendar/) 
* Nesta [Makerspace Overview and Map](http://www.nesta.org.uk/blog/top-findings-open-dataset-uk-makerspaces)
* Look at the [Hackerspace List](https://wiki.hackerspaces.org/List_of_Hacker_Spaces) to find Maker Spaces in the North https://wiki.hackerspaces.org/List_of_Hacker_Spaces
* Other kinds of making space with some public access, [Fab Labs Map](http://www.fablabsuk.co.uk/making-spaces-in-the-uk/)
* Contact e-NABLE directly, [Enabling The Future](http://enablingthefuture.org/) the glogal project whose designs we are using and modifying have a system to help pair people with making spaces
* [Reach](http://www.reach.org.uk/) in the North West

### When and Where is it Touring to?

*Build Your Own* and *DesktopProsthetics* is touring to [Norwich Castle Museum & Art Gallery](http://www.museums.norfolk.gov.uk/Visit_Us/Norwich_Castle/index.htm) from *3 October 2015 to 3 January 2016*. For that time the project will be supported by [Norwich Hackspace](http://www.theshiftnorwich.org.uk/norwich-hackspace.html) not DoESLiverpool alongside [Norfolk Museums Service](http://www.museums.norfolk.gov.uk/) and the [Crafts Council](http://www.craftscouncil.org.uk/what-we-do/build-your-own/)

### What limits are there, if any, with 3D printing?

Like any manufacturing technique, 3d printing has its advantages and disadvantages.  3d printing also covers a range of different techniques, and possible materials, with the resulting printers ranging in price from a few hundred pound into tens of thousands of pounds.

As the Enabling the Future project is geared towards democratising access to prosthetics, we're using printers from the more affordable end of the range which print in plastic (rather than resin or metal).  This type of printing can only print in one or sometimes two colours of material at a time; and while the prints are surprisingly robust, the printing technique gives the models a sort of "grain" - like you get in wood - where it's weaker when subject to forces along that grain.

### What are Makerspaces?

What exactly is a makerspace? Using the term broadly, we’re talking about public spaces or small volunteer run membership organisations with different tools and equipment where people can go to independently make something or meet potentially like minded people. While we need to appreciate the diversity of these spaces, it’s also important to think beyond formalised networks (like Fab Labs) and focus on spaces defined by a specific ethos (like Hackspaces). So Fab Labs have similar facilities in common with maker spaces and hackspaces but alot more formalised and less community led to a varying degree. DoESLiverpool has things in common with say HacMan but also includes a co-working space to support their facilities and also is a home for not just making but tech culture in general supporting IoT Liverpool, Startup clups and coder dojo's all led and run by local(and not so local) interest groups/affiliates/organisers/hot deskers/permanent desk people or just members of the google group mailing list interested in running something.

Hannah Stewart at the **Creative Exchange** has been doing some very detailed open research into the area which is linked from [this introductory blog post](http://www.nesta.org.uk/blog/top-findings-open-dataset-uk-makerspaces)
also worth checking http://www.hackspace.org.uk/wiki/Main_Page and http://hackerspaces.org/ (for a global list of hackspaces)

DoESLiverpool like many makerspaces and hackspaces, as an organisation do not do projects in a sense, we simply help our community to realise their projects with the facilities we have. Our community is essentially anyone who wants to do something with us.

As said above this collaboration with FACT was inspired by a member of our communities interest: the 3 'leaders' of the project have interests and skills in 3D printing, which is why it's happening. If nobody in the community wanted to do it, it would not happen. If a group grows and develops around the activity in the exhibition then that group can continue to use DoESLiverpool and the new printer to support it like the many diverse groups that call DoESLiverpool home.

This is a common theme in many maker and hackerspaces: somebody donates or stores some kit permanently or temporarily and then often more and more people start to use it and interest groups can (but not always) build around things like this. Also there is a general openness across these spaces although at the same time a haven for people interested in certain things.

For instance @cheapjack recently setup a small exchange between a hackerspace in Bochum, Germany DasLabor and DoESLiverpool which you can see more about here. Like DoESLiverpool they are primarily a member led space for their community but do come together for events like DesktopProsthetics and Maker Faire UK to let the wider public know about what they do.

### Describe in a few words the processes that went into making the work?

The process was a gradual design of the format of the project between DoES Liverpool and FACT with the BuildYourOwn team of designers producers and curators. To make this work we forced everyone onto github which we hope will format things nicely for Norwich hackspace and other people to refer to: github itself is the sort of tool that has come from the growth of open source tech cultures. GitHub (and git) can be used as a tool (like a wiki) for open sourcing something. The format and context of the project was setup by permanent deskers Adrian, Ross & Patrick of DoES Liverpool and then the work will be realised by both  Reach, FACT and DoESLiverpool feeding in a user base into the DesktopProsthetics space. FACT gallery guides will produce the work, supported by Adrian McEwen, Ross Dalziel and Patrick Fenner.  

DoESLiverpool like many makerspaces, do not **do** projects in a sense, we simply try to **help our community to realise their projects with the facilities we have.** Our community is essentially anyone who wants to do something with us. This collaboration with FACT and Reach originated from a local family printing a prosthetic hand in our workshop and 3 members of the community leading the project, with interests and skills in 3D printing suggesting that building on this was a good idea.

I'd say the background to why this kind of project has happened the way it has, is the growth of maker/hacker spaces and open source thinking and their emergence into the mainstream; plus more and more public facing events like Maker Faire UK, cultural and civic hackdays combined with open tools like github or sharing platforms like thingiverse that makes it easier to work like this. There's a rising awareness of this kind of 'open' technical culture being a conduit for change not just individual experience and need but the wider infrastructure of society itself and the things that it uses and makes.

### The Raptor reloaded prototype is designed for someone with a working wrist joint, what if I don't have one? Can I still print a hand?

**An issue** that came up at the [Measuring Workshop](https://github.com/cheapjack/buildyourown/blob/master/events/MeasuringUpWorkshop.md) was that we realised that for many people, the [Raptor Reloaded](http://www.thingiverse.com/thing:596966) design which we’ve been using for the project may not be the most appropriate design for everyone's situation; it's designed for some kind of wrist joint to make it work mechanically. As we originally only had experience building this design it made us have to re-think things.

First off we are going to continue printing out prototype hands for those that seem best suited based on our groups experience and advice (Drew, DoES, e-NABLE, Baylee and family). They are currently in the FACT print queue getting printed out ready for assembly in August.

If, in your case you don't have a conventional wrist joint we've come up with this plan.

 * Print out a Raptor reloaded hand for everyone and look and see how it could be adapted for you at the assembly workshops on the 8th and 22nd of August. This is the best option as we have a working scaling system for the Raptor design and it will give us something to start with. We have been researching the 'Raptor Wing' which is an adaptation to help make the Raptor design work for someone with no or limited wrist use and for a range of forearm sizes.

 * One family from Devon took a raptor demo hand with them (mainly as they'd travelled all the way from Devon) and their son only had an elbow joint with very short forearm; as a starting point they were happy with that option and their son did get use of it and enjoyed having one despite him having no wrist joint. They will also have their details passed onto e-NABLE, like all of us, to connect to their community.

 * Experiment printing out an example Raptor Wing and also the ‘RIT-Arm’ prototype and experiment fitting them with the Raptor hands at both of the assembly workshops on the 8th and 22nd August 2015 at FACT. We have to acknowledge we have no experience with these designs but the Raptor Wing looks like the most promising, esp. as it allows us to use the Raptor hands that we do know about. The RIT-arm fitting relies on fitting a cup that will accommodate people’s limbs so its hard to do this without making one and trying it out and it won’t be the right solution for everyone

 * It may be that not everyone's hands will be ready for assembly on the assembly days (8th & 22nd August) but we will update you all closer to the time (approx. Saturday 1st August) so we can confirm you will have something to assemble and work with and this will help you to decide which day to come on if you can only come to one.

We **can't guarantee** that after the assembly workshops everyone will go away with a hand that works in the best way for them but it is a starting point in the *prototyping process*. Moving on from there people can join the interest group which we hope will develop around the project, so you can print more prototypes and make adjustments yourselves and also take up a dialogue with e-NABLE and other participants of **DesktopProsthetics.**

At the moment we have compiled everyone's measurements and reference hand images and have used Drew Murray's experience knowledge and advice to make this plan. 

We will carry on printing and update participants from the first Measuring workshop on progress by **August the 1st 2015**.

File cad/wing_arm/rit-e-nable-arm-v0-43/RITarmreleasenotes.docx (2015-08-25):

# RIT Arm Documentation

("Derek Arm version")

Second release v0.43 July 29 2014

Jascha Wilcox

Paul Richard

Jon.Schull@RIT.edu

Disclaimer

License

Overview

The Current Model

Customization for other individuals.

Typical Fabrication and Assembly Procedure

I. Print components

III. Assembly

IV. String it up

V. Fitting

Revisions

## Disclaimer

By accepting any design, plan, component or assembly related to the so called “RIT Arm”, I understand and agree that any such information or material furnished by any individual associated with the design team is furnished as is without representation or warranties of any kind, express or implied, and is intended to be a gift for the sole purpose of evaluating various design iterations, ideas and modifications. I understand that such improvements are intended to benefit individuals having specific disabilities and are not intended, and shall not be used, for commercial use. I further understand and agree that any individual associated with the e-NABLE organization shall not be liable for any injuries or damages resulting from the use of any of the materials related to the e-NABLE Arm.

## License

This arm is licensed for non-commercial use, subject to the disclaimer above.
Commercial licenses are negotiable.

We currently use fingers from Jorge Zuniga's Cyborg beast design, which is subject to it's own non-commercial use license. See http://www.thingiverse.com/thing:261462

## Overview

The Derek Arm is an elbow-actuated variant of an RIT-developed e-NABLE prosthesis designed to fit Derek, the first user of our arm. As illustrated below and in the video at http://www.youtube.com/watch?v=T9nngOrdPkg, bending the elbow causes the fingers to flex by tightening strings descending from the fingers to tensioners in the upper arm.

## The Current Model

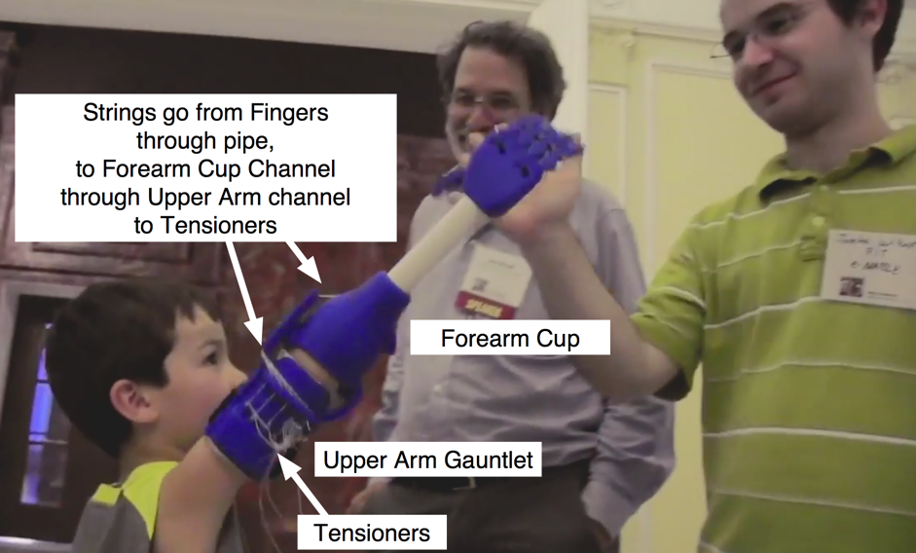
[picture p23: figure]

The Derek Arm prosthesis requires more customization than an e-NABLE Hand, because it replaces a portion of the forearm, is larger and more complicated, and is subject to greater forces. Furthermore, the interior of the forearm cup will typically be custom shaped to fit a particular individual.

This is a work in progress and we are aware of the limitations of an elbow-actuated design: because it links arm-bending to hand-closing, it imposes limits on the extent to which the arm can be bent, and it puts additional force on the forearm. We expect that an actuator like a scapular harness will be a more robust solution. (But Derek, our only user, reportedly really likes what he's got!)

We suggest you contact us to check for updates and improvements before proceeding to make an arm for a recipient.

## Customization for other individuals.

You will probably want to ....

- Import the IGS or STP files into a modelling program such as Inventor, Solidworks, or Fusion 360.
- Re-proportion the Upper Arm Gauntlet and Forearm cup to match your recipient.
- Ensure that the interior of the Forearm cup is a good fit for the recipient's Forearm. [see: Customizing Forearm Cups (https://docs.google.com/document/d/1nX6Jt51XNMu29M--agSNmPBqvqLpu98dOMyuvXja2xc/edit)]
- Ensure that bolt-holes and PVC pipe hole diameters match the bolts and PVC pipes you intend to use:

Chicago Screw bolt holes diameter : 0.210” OD

PVC pipe holes (assuming 3/4" PVC) diameter : 1.050” OD

Materials

Category | Item | Quantity | Fabrication time (FDM)
Printed parts | Forearm Cup | 1 | 6-10 hr
| Palm | 1 | 2-4 hr
| Upper Arm Gauntlet | 1 | 6-10 hr
| Finger proximal | 4 | 2-3 hr
| finger distal | 4 | 2-3 hr
| thumb proximal | 1 | ~30 min
| thumb distal | 1 | ~30 min
| hex tensioner | 5 | ~15 min
| PVC retainer Ring | 1 | ~45 min
Hardware | Chicago Screw 2.5" Al (knuckles)* | 1 | -
| Chicago Screw 3/8" Stainless (proximal/distal joint)* | 5 | -
| Chicago Screw 1/2" SS (thumb and elbow pivot) | 3 | -
| Beads | 15 | -
| Thin strong fishing line (http://www.walmart.com/ip/17113497?wmlspartner=wlpa&adid=22222222227000000000&wl0=&wl1=g&wl2=c&wl3=41833582510&wl4=&wl5=pla&wl6=19880599990&veh=sem)* (e.g., Izorline Premium Dacron Fishing Line) | 5 | 5 min
| Elastic bands | 5 | 5 min
| Tensioner screws (varies) | 5 | -
| Buttonhead woodscrew 4 (or Tensioner screws) for PVC retainer ring | 6
| PVC Pipe 3/4" (1.050” diameter)* | 1 | 5 min
| Velcro | 1 | -
| Firm foam padding | 1 | -
| Loctite 242 (blue) threadlocker* | 1 | -

*These components are NOT included with the Cyborg Beast assembly kit from 3D Universe, as of June 24, 2014

Tools

Cordless drill (or manual tap handle)

Heat Gun

Drill bits

Miniature files

"Threader" (http://youtu.be/gaRp_Ma73_E)

Needle-nose pliers

Sand paper

Screw drivers

Hobby knife

Scissors

Hack saw/Tubing cutter

## Typical Fabrication and Assembly Procedure

### I. Print components

  - Check the scale of the parts. The provided STL files are in mm scale, binary format. Most 3D printer control software assumes mm scale by default, so the parts should import correctly. If you modify the parts in CAD and export them again, be careful to specify that the part is in the mm scale.
  - Check tolerances. This device currently uses a press fit around the PVC pipe in the palm and forearm cup components. This means that diameter tolerance on the 1.050” mating holes are on the order of +/- 0.005”. It may be necessary to modify the part to compensate for printer variations.
  - Use Preview in your slicer to make sure internal channels are empty. The channels are curved inside the palm so you will not be able to drill them out.
  - Print the components! Nylon or ABS plastic is recommended.

II. Post-process printed components.

  - Remove support materials. A pair of needle nose pliers, a small file, and some sandpaper is generally sufficient to remove support material.
  - Check Chicago screw hole diameters. If holes are too tight you can enlarge them with a drill or hand tap handle.

### III. Assembly

- Assemble fingers and thumb. Use 4x ⅜” stainless chicago screw for the four finger joints, and 1x ⅜” stainless screw for the thumb finger joint. Then use loctite threadlocker.
- Attach fingers and thumb to palm. Use 1x 2 1/2” screw (or modify length for a re-scaled palm)
- Attach the forearm cup to the upper-arm gauntlet using 2 x ½” stainless Chicago Screws.
- Cut the PVC pipe to the correct length using a hacksaw. Usually it is best to try to match the length of the other arm, but Derek specifically requested an “extra long” version. Sandpaper can also be used to remove any writing on the pipe.
- Add a flange to the PVC pipe. Use heat gun to soften one end of the PVC pipe and use a hand tool that will not melt, to bend the PVC out as illustrated here:

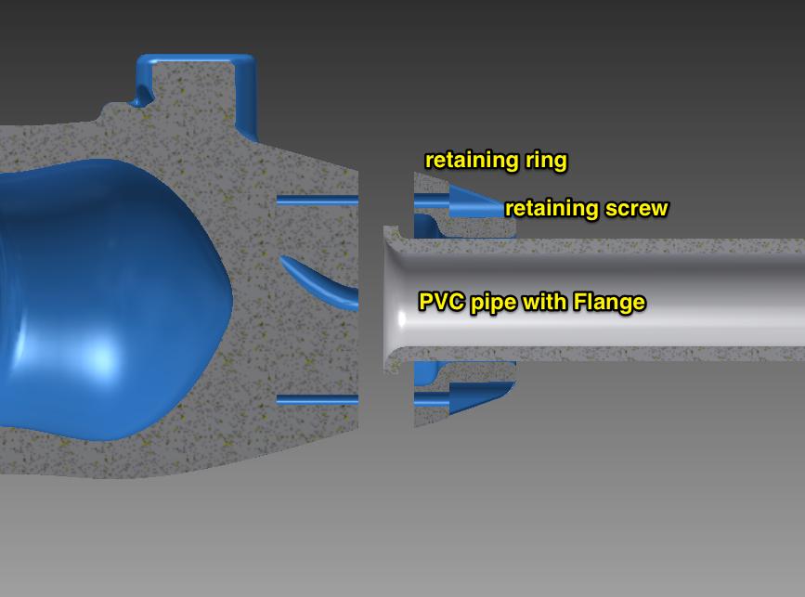
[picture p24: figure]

The flange fits into the 3D printed PVC Retainer component, which screws on to the Forearm Cup component.

- Insert hex tensioners in tensioner sockets. Secure with a couple turns of a tensioner screw. You will adjust the tensioners later.

### IV. String it up

A “threader” wire is extremely helpful, as illustrated in this video: http://youtu.be/gaRp_Ma73_E

- Thread elastic bands through the channels on the backs of the fingers and thumb, through the palm.
  - Use beads to terminate the elastic bands.
- Thread fishing line through the under-channels of the fingers, and through the internal palm channels.
  - Use beads to secure fishing line at each finger tips.
  - Leave more than enough loose string to reach the tensioners on the Upper Arm Gauntlet
- Thread fishing lines through PVC pipe.
- Press PVC pipe into Palm socket
- Thread fishing line through the Forearm Cup channel
- Thread fishing line through the Upper Arm Gauntlet channel
- Route fishing line from through the tensioner channels to the tensioners.
- Tie off fishing line at tensioners, adjust tension. Test and adjust, test and adjust.

### V. Fitting

- The fine art of fitting and padding prosthetics is beyond the scope of this documentation. [see: Customizing Forearm Cups (https://docs.google.com/document/d/1nX6Jt51XNMu29M--agSNmPBqvqLpu98dOMyuvXja2xc/edit)]

Please consult a prosthetist, use skin-safe padding, watch out for redness, chafing, or muscle strain, and make sure recipients understand that this is an experimental device for evaluation purposes. See

Make sure recipients understand and sign the Disclaimer above.

## Revisions

- June 24, 2014: First release, v0.3 with documentation.
- July 28, 2014: Second release, v0.43, with the following improvements over v0.3
  - Hyperextension stop
  - pull-pull portals for active opening fo the hand

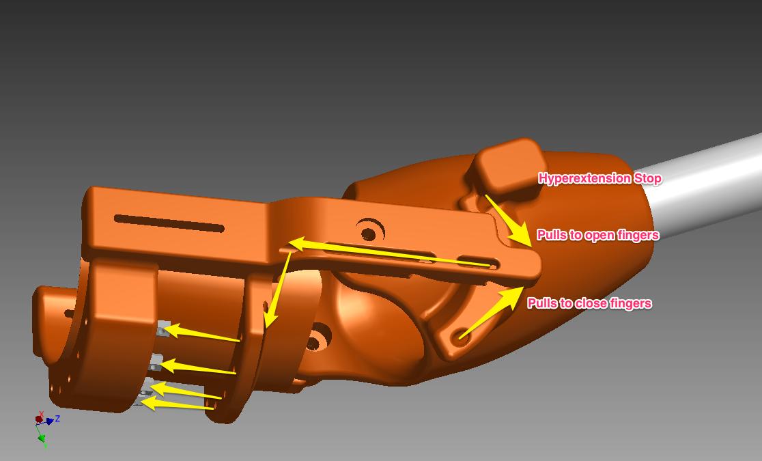
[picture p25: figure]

  - PVC Flange Lock

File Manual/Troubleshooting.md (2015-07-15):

### The filament is stuck and won't progress past the extrusion head

Try the `cold-pull` method as outlined [here](http://support.3dverkstan.se/article/10-the)

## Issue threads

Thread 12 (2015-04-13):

cheapjack/buildyourown #12: Get all exhibition presentation completely cemented with the Bloors this week

cheapjack, 2015-04-13:
Be great to get all exhibition presentation completely cemented with the Bloors and us this week so they can order all materials (they're getting worried about import dates etc). I am also going to send you the draft of the exhibition credits etc today, and would be great if I can get those back by the end of the week with any additions or amends you need to make.

amcewen, 2015-04-13:
Is the best way forward with this a conf call, or does it make more sense to spec out what will be on each plinth, etc. in more detail and use that to drive the requirements?

(Thinking out loud here - might need both for it to be a productive conf call...?)

cheapjack, 2015-04-15:
Hi I think we are happy to raise issues and tasks toward the exhibition design and Simon & Tom are responding to issues on there (thanks guys!) now. I've updated the [main exhibition setup document](https://github.com/cheapjack/buildyourown/blob/master/Exhibition/FACT/FACTSpaceSetup.md) to be a bit clearer on numbers of pegboard panel sections(4) to number of hit and miss panels(5).

I dont think we need a conference call or anything now. Just comment or raise an issue if you have any things that need resolving guys @bloors :+1:

cheapjack, 2015-04-27:
The Bloors updated ideas on space setup last week which we need to comment on. This is the first option embedded below that look the best but unsure on the module (prob for a text panel) that splits up the space. Its a decent sized space we can add tables/seating if required to accomodate Amy's concern on numbers on the Measuring workshop.

Ive updated the exhibition setup file to include

[image]
[image]

cheapjack, 2015-04-27:
Need to comment on "We're looking at options for the story plinth, we've got three at the moment, one's a long linear one along a wall, the second comes out from the wall (fixed) at 90 degrees but is more like a table with objects viewed from two sides, and the third is a free stranding table. there is room for wheelchair access all the way around, we're thinking the height will be 700mm, about the height of a table, but it could be up to 800mm high, I'd say any lower than 700mm is getting a bit too low for viewing objects for most standing adults. 
We're imagining the objects will be on the 'sub plinth' panels on the table top with space for any interpretation texts next to each block. The size (and number) of these is flexible but we need to work out the overall dimensions so we can get the bigger MDF sheets and the metalwork all pre-cut. the scaffold fixings will be different depending on the arrangement so this needs working out soon. 

Also if any of the objects need to be in vitrines the dimensions need confirming soon so these can be ordered.

Do you have preference to the layouts below? the first long 'bench' type version does leave a lot of empty room in the space which the Fact gang didn't think worked so well, but it's more like the previous designs we've discussed.

Cheers
Tom"
*Option 1*
[image]
[image]
*Option 2*
[image]
[image]
*Option 1*
[image]
[image]

almataki, 2015-04-27:
I think conceptually options 2 and 3 are much more interesting in the space. being able to walk around the storyplinth rather than sticking them into a line by the wall.

cheapjack, 2015-04-27:
Ok I think option 3 works better then: you can get round the back of the story table with that one then and still find space for extra people... I'm assuming all the green area is for us, the screen in the middle of the space seems superfluous and splits the story from the production bit on the other side so not sure it's a good idea? Also I cant quite see the orientation; ie where the G1 window is?

LesleyTaker, 2015-04-27:
The G1 window is closest to the table with seats on, where the printers
are: that runs all along the wall which also runs along the ramp into G1.

-- 

Lesley Taker
Curatorial Co-ordinator
FACT (Foundation for Art and Creative Technology)
88 Wood Street
Liverpool, L1 4DQ

Please note, I am only in office until 3pm on a Friday.
tw: @lexy_taylor
t: + 44 (0)151 707 4419
f: + 44 (0)151 707 4445

http://www.fact.co.uk
Admin: +44 (0)151 707 4444
Bookings: +44 (0)871 902 5737

*FACT - Bringing people, art and *
*technology together since 2003*

--------------------------------------------------------------
--------------------------------------------------------------

*Group Therapy: Mental Distress in a Digital Age5 March – 17 May*

Originating from FACT’s extensive work within

mental health and wellbeing, the exhibition

explores the complex relationship between

technology, society, and mental health.

--------------------------------------------------------------
--------------------------------------------------------------

bloors, 2015-04-27:
Hi Ross 
Just to clarify: the window doesn't overlook your space, it's in Will Shannon & Assemble's area (in red). And yes, all sides of the story table can be accessible.
The screen bit is in keeping with the design through the show and is for the info for your project. It'll include the A2 interpretation panel and guide leaflet rack, a TV/monitor with your film on and the map inphographic (on the double boards), so needs to be that scale and placed there. We've deliberately split the two spaces so exhibition visitors can still look at the story table while the workshop sessions are going on in the other area. 
Best,
Tom

www.simonandtombloor.com

cheapjack, 2015-04-28:
Ok I see Tom makes sense in that case let's keep the layout as it is then I think it will work great! In that case lets **go for layout Option 3**

amcewen, 2015-04-28:
I'm happy with @cheapjack's choice of option 3, just wanted to pick up on two points:

First, the pieces which need to be in vitrines are all listed in the "5 steps to a new hand" sections of https://github.com/cheapjack/buildyourown/blob/master/Exhibition/FACT/FACTSpaceSetup.md

Secondly, we're having a TV/monitor to show a film?  What film is that?  Am I forgetting something?  (Quite possible :-)

cheapjack, 2015-04-28:
Yes I did not realise we were showing a film....assumed that might not apply to this as would need to involve so many partners etc.. Seems like could be a fair bit of work that! Is this something that FACT are making like the film made for Cloudmaker?

bloors, 2015-04-28:
Hi
The film is one (we've been told) is being made, one for each exhibitor/group, think it's an interview. Alma knows more about it I think (I hope someone does..!)
Will check over your info, thanks.
Tom 

www.simonandtombloor.com

cheapjack, 2015-04-28:
We all happy with the printers on a freestanding table by as in Option 3? Im also guessing this area of the layout should be pretty much be all pegboard for flexibility hanging storage boxes. Its looking like we will likely have 3 printers now (2 bought, one borrowed) but with each a footprint of  W 338 x D 358 x H 289 mm I think they will be fine.

[image]

bloors, 2015-04-28:
Hi
Actually that’s an old design, sorry for the confusion. The printers are on a wall mounted shelf as originally discussed, see below. 
The shelf is 700mm deep and 2440mm wide so plenty of room for three printers. If you like it could be deeper so there’s more space in front of each printer.

best,
Tom

> We all happy with the printers on a freestanding table by as in Option 3? Im also guessing this area of the layout should be pretty much be all pegboard for flexibility hanging storage boxes. Its [...]

Simon & Tom Bloor
44(0)7866274975
Grand Union Studios
Unit 15 Minerva Works
158 Fazeley Street
Birmingham
B5 5RS
simonandtombloor.com
kiosk1and2.org

bloors, 2015-04-28:
This is the pic, not sure it was sent here
[image]

cheapjack, 2015-04-28:
Great! that works better and pegboard looks good I *think* that's enough pegboard how many hookable boxes did you get in the end?  if they all fit the pegboard then should be fine. Also we should run power up or down the inside of the panels depending on Mark at FACT's recommendations

cheapjack, 2015-04-28:
I've updated the [space setup md file](https://github.com/cheapjack/buildyourown/blob/master/Exhibition/FACT/FACTSpaceSetup.md) now with the correct images

LesleyTaker, 2015-04-29:
It is the film which @almataki mentioned, documenting one element of the
process / a bit of the workspace etc. All of the artists are having some
form of documentation of at least one element of their work. She is trying
to tie down dates with the filmmaker for Liverpool atm.

-- 

Lesley Taker
Curatorial Co-ordinator
FACT (Foundation for Art and Creative Technology)
88 Wood Street
Liverpool, L1 4DQ

Please note, I am only in office until 3pm on a Friday.
tw: @lexy_taylor
t: + 44 (0)151 707 4419
f: + 44 (0)151 707 4445

http://www.fact.co.uk
Admin: +44 (0)151 707 4444
Bookings: +44 (0)871 902 5737

*FACT - Bringing people, art and *
*technology together since 2003*

--------------------------------------------------------------
--------------------------------------------------------------

*Group Therapy: Mental Distress in a Digital Age5 March – 17 May*

Originating from FACT’s extensive work within

mental health and wellbeing, the exhibition

explores the complex relationship between

technology, society, and mental health.

--------------------------------------------------------------
--------------------------------------------------------------

amcewen, 2015-04-29:
Cool, I'm sure the film's been mentioned, but probably didn't lodge in my brain as it wasn't something we needed to deliver :-)

@cheapjack Are we putting all three Ultimakers into the gallery?  I thought the one we were borrowing was mostly to cover the 3-4 months when the other printers are in Norwich so we can finish off any support for the NW participants (and give us some more capacity for printing out hands at the start)?  In which case, there'd only be two going down to Norwich, so do we want to make room for them in the gallery in Liverpool too?

almataki, 2015-04-30:
Hi again. We are working with Jared Schiller http://jaredschiller.co.uk/ and he just confirmed he can come up to Liverpool on May 15th. Might you be around to do some filming with him? talk about the project, DoES, the community and your process?

amcewen, 2015-04-30:
I don't think any of us are around on the 15th, I'm afraid. @cheapjack 
and I are over in Sheffield IIRC, and Patrick generally has childcare 
duties on a Friday.  Is he likely to be up any other dates?

almataki, 2015-04-30:
hmmm would the 16th be any better for you? are you available any other day of w/c 11th May?

cheapjack, 2015-04-30:
My mistake we are in Sheffield on Saturday only: the 16th may, had looked at wrong month somehow so 15th would be ok for me at least as well be in does that day anyway preparing for the Saturday if that would work

almataki, 2015-04-30:
OK this is great news! I wasn't sure Jared would be able to come on a different day and also Will Shannon will be doing concrete casting on Cairns Street that day so it fits very well. Any time that works for you? and is there a number that Jared can use to contact you on the day?

almataki, 2015-05-12:
@cheapjack Jared will be in Liverpool this Friday. Shall I tell him to come and meet you straight at , Gostins Building, 4th Floor. 32-36 Hanover Street. Liverpool L1 4LN ? His number is 07916 168 141 if you need him on the day. What times you'll be around on the day?

cheapjack, 2015-05-12:
Hi mid morning or early afternoon would be ok for me

almataki, 2015-05-13:
Jared arrives at the station 12:20pm so he will be at your studio at 1pm. Is that OK?

cheapjack, 2015-05-13:
That sounds OK by me 1pm is ok maybe could combine with lunch but not sure on availability of @amcewen & @defproc I know @defproc maybe on child care duty that day . it could just be me going over design which is fine by me :) and can pickup any issues my number is 07977406552 for him

amcewen, 2015-05-13:
I should be around then.

almataki, 2015-05-14:
Very small change of plans Jared will be with you about half an hour later as he has to go elsewhere first. hope that's ok.

LesleyTaker, 2015-05-18:
Hi all, just to ask a space related Q: do all of the story plinths need vitrines? Even the iPad? Is this not a problem for if it crashes or anything and it having to be moved? Also, what height were you thinking? Just to reiterate the footprint of the subplinths on the table are 500mm x 420mm FYI

LesleyTaker, 2015-05-20:
Hey, just wondered if I could push you guys a bit on this? I need to order the vitrines by tomorrow in order to make sure we receive them in good time!! Just need confirmation of number and height! L

amcewen, 2015-05-20:
It's four vitrines in total - they're listed in the steps that need them on https://github.com/cheapjack/buildyourown/blob/master/Exhibition/FACT/FACTSpaceSetup.md :-)

So the iPad doesn't need one (we're assuming it'll be tethered to the plinth but something people can pick up and play with), and if they're at least 10cm high that'll be fine (I don't know what sort of sizes vitrines come in...)

closed 2015-05-20 by amcewen

cheapjack, 2015-05-20:
I think Lesley you have what you need now; I've started a [template for vinyl artwork required for the vitrines and plinths in pdf and svg format](https://github.com/cheapjack/buildyourown/tree/master/Exhibition/FACT/interpretation) so @LesleyTaker could you just have a final look at the dimensions of the overall and individual sub-plinths [here](https://github.com/cheapjack/buildyourown/blob/master/Exhibition/FACT/interpretation/Vitrines.pdf) and check they are right so I can layout the vinyl to fit amongst the objects/hand parts etc.
 
We will only need a maximum or 4 vitrines @LesleyTaker and I will be prepping & applying the vinyl to the plinths when they ready. I don't know whether plinths sit over/around the subplinth footprint or not but as long as they give us the minimum height clearance of 10cm (between subplinth and vitrine surface) we will be fine.

I think on a standard entry in to G1 you would approach the vitrines in a way that would mean you'd read Vitrine 1 first: we can always turn the table round if it does not. 

Artwork will live here once Ive finished it
https://github.com/cheapjack/buildyourown/tree/master/Exhibition/FACT/interpretation

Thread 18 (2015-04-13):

cheapjack/buildyourown #18: Do we need to secure the calipers on display?

amcewen, 2015-04-13:
For the first step in "5 steps to a new hand" we'll have a set of measurement calipers and an Android tablet.  

As the tablet is something for people to pick up and interact with, it doesn't feel like a vitrine is right for that step's display.  However, does that mean the calipers are likely to go missing?  Do we need to do anything to prevent that?

cheapjack, 2015-04-13:
Maybe calipers and other things can be secured on the pegboard backing by the printers or above the measurement shelf until needed and gallery assistants help get tools when needed.. Means the gallery assistants (GA's) are a bit like store keepers

amcewen, 2015-04-13:
These aren't calipers for using, they're calipers to be on display to explain the steps you go through to get your new hand.  So that's another reason to secure them on the display, so they don't get stolen to be used in measuring things up for a workshop! :-)

bloors, 2015-04-14:
They should probably be secured, either on pegboard or to the shelf....Linda Brothwell is using the pegboard to display the tools she's made–they will be secured so people can't take them. For your space we could have a mix of secured tools (above '5 steps' shelves) and tools that can be used (above printers or elsewhere). Or we could look at attaching tools to the shelves in some way, but use smaller bits of the coloured MDF to display them in a more museological way...
[image]

DefProc, 2015-04-14:
How's 'wired to the pegboard'?

amcewen, 2015-04-15:
There isn't any pegboard behind the 5 plinths, as that's where the explanation text will be.  Plus I think the calipers should live next to the tablet.

Maybe we can drill a couple of holes in the plinth and then wire/cable-tie the calipers onto the plinth?

DefProc, 2015-06-05:
No calipers on display, just a vinyl.

closed 2015-06-05 by DefProc

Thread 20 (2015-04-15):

cheapjack/buildyourown #20: How do members of the public try out wearing a prosthetic hand?

amcewen, 2015-04-15:
We'd mentioned having some stuff for people to try picking up, etc. 

What are those things?  Where do they live?  On the table in the middle?

cheapjack, 2015-04-15:
I think on the table, but with a storage box set apart from the others & labelled, so
* Printed 'example' hand
* finishing/clipping and sanding tools
* Custom 3d printed dowels for finishing: we had initially talked about an UP printer (which prints with deifferent spec material) on the table making these useful tools

LesleyTaker, 2015-04-16:
Do we still want the UP? Love the idea of having useful bits on the table.
Hannah, the curator from Norwich, had worries about them going missing
though, so maybe we have a way to attach? Or any ideas around this?

-- 

Lesley Taker
Curatorial Co-ordinator
FACT (Foundation for Art and Creative Technology)
88 Wood Street
Liverpool, L1 4DQ

Please note, I am only in office until 3pm on a Friday.
tw: @lexy_taylor
t: + 44 (0)151 707 4419
f: + 44 (0)151 707 4445

http://www.fact.co.uk
Admin: +44 (0)151 707 4444
Bookings: +44 (0)871 902 5737

*FACT - Bringing people, art and *
*technology together since 2003*

--------------------------------------------------------------
--------------------------------------------------------------

*Group Therapy: Mental Distress in a Digital Age5 March – 17 May*

Originating from FACT’s extensive work within

mental health and wellbeing, the exhibition

explores the complex relationship between

technology, society, and mental health.

--------------------------------------------------------------
--------------------------------------------------------------

cheapjack, 2015-04-28:
I think we do... even though now we should have a borrowed 3rd ultimaker printer we need a list of the tools but maybe wont know what these will be until we start printing the example hand as soon as we get the printers, unless Jason Abbott had any suggestions @amcewen meeting him tomorrow so if he sees this then we could ask. 

Sanding blocks and dowels you can wrap sandpaper in seem useful need to make a few designs but could include a hoop on each that stays clipped to the table for security maybe...for small items if they go missing, then we print more and it gives another thing printing for people to watch...or when they not used the go in the pegboard hanging box for tools. Actually not many people even think you need tools to finish off some printed stuff; so be good to show that.

LesleyTaker, 2015-04-29:
We can always still use the UP but locate it in the FACT Lab in G2? Just
for safety / space sake?

-- 

Lesley Taker
Curatorial Co-ordinator
FACT (Foundation for Art and Creative Technology)
88 Wood Street
Liverpool, L1 4DQ

Please note, I am only in office until 3pm on a Friday.
tw: @lexy_taylor
t: + 44 (0)151 707 4419
f: + 44 (0)151 707 4445

http://www.fact.co.uk
Admin: +44 (0)151 707 4444
Bookings: +44 (0)871 902 5737

*FACT - Bringing people, art and *
*technology together since 2003*

--------------------------------------------------------------
--------------------------------------------------------------

*Group Therapy: Mental Distress in a Digital Age5 March – 17 May*

Originating from FACT’s extensive work within

mental health and wellbeing, the exhibition

explores the complex relationship between

technology, society, and mental health.

--------------------------------------------------------------
--------------------------------------------------------------

amcewen, 2015-05-30:
Okay, we're printing off some hands in different sizes, so that people can try them on.

We'll have at least one at 65mm (Baylee-sized), one at 90mm (demonstration_adult), one at 80mm.

cheapjack, 2015-05-31:
Drem Murray will be lending us some other designs also so we will have plenty of things for the public to see and try out, managed by the gallery guides of course.

closed 2015-05-31 by cheapjack

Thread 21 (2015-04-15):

cheapjack/buildyourown #21: Exhibition Text Panel

almataki, 2015-04-15:
I'd just like to flag sth up. 
As you can imagine the curators are putting together texts/captions for the projects in the show and for the gallery guide etc. These are a bit different to the marketing print and aim to provide a wider context/background to the work (as all exhibition texts do). We are still editing those heavily but I plan to share them with you on Monday next week (20th April) advance of sign off  for Friday (24th April). 
Each project gets one panel of about 150words + credits and urls and then the same text will be used in the printed gallery guide together with biogs. All this to be shared with you on Monday. The text will be based on your copy from README and does not reference Baylee.

almataki, 2015-04-15:
To add to this the panel texts will be etched into 3mm engraving laminate-layers of white and black acrylic stuck together. An engraver then cuts down through the black to leave a relief of white text. The panels will be attached to a pegboard panel. So each project will have at least a single width pegboard with a white letters in black acrylic panel about A2 in size.

amcewen, 2015-04-15:
Cool.  That sounds good.  Is that laser-engraved or CNC milled, do you know?  (Just curious :-)

almataki, 2015-04-17:
Adrian I asked the guys to clarify but haven't heard back. 
In the meantime, can we start with your biog? I drafted the below but it should be a bit longer and it would be nice to include some of your past projects. We've done this for the other artists' biogs listing a few older exhibition etc. However it should be longer than 80-100words tops.

DoES Liverpool
DoES Liverpool is a community of makers and entrepreneurs with a diverse range of skills of interests. DoES founding members include creative technologists and developers Adrian McEwen, John McKerrell, Hakim Cassimally, Paul Freeman, Andy Goodwin and Ross Jones. The community includes a co-working space, workshop, event hub, and much more. *[to add past projects]* www.doesliverpool.com

Do you think we should include a biog- or more like an about text for e-NABLE?

Thanks!

almataki, 2015-04-17:
correction: It should NOT be longer than 80-100 words tops

almataki, 2015-04-17:
OK so this is where the caption text currently stands, please check the crediting and let me know if you'd like to add anything. The caption shouldn't be more than 200words.

**Desktop Prosthetics (2015)**
DoESLiverpool: Ross Dalziel, Patrick Fenner and Adrian McEwen
??E-nabling the Future network??
??Norwich Hackspace??

Hacker and entrepreneur community DoESLiverpool presents an iteration of the open-source project E-nabling the Future, a project that allows people across the world to build prosthetic hands using 3D printers. e-Nable is a worldwide movement of tinkerers, engineers, 3D print enthusiasts, occupational therapists, university professors, designers, artists and families who work together to build simple, low-cost devices for people in need of prosthetic limbs or to guide them as they build one themselves. 
Inspired by a local family who used DoESLiverpool's workshop to print hand parts independently, DoES has installed a ‘production line’ for prosthetic hands using 3D printing technology and open-source designs. *[more about the ethos of DoES, the philosophy of Open Source, Creative Comms and decentralising production and bringing communities together to teach one another and trade skills in an equal, free-trading style environment.]*

Over the course of the exhibition, DoES in Liverpool and Norwich Hackspace invite you to get involved in testing and building prosthetics, experiment and understand what prosthetics are and how access to rapid prototyping and open source digital making tools can help people make the world the way they want it. Check the events panel for more details of how you can take part.
*[also add something for visualisation? – CC needs to confirm this]*

*[other credits]- This is for anyone or any other organisation you’d like to credit and it’s not mentioned in the text*

www.doesliverpool.com
www.enablingthefuture.org

almataki, 2015-04-17:
And sorry this is all done in a hurry and I'm well aware you guys have a lot on your plate already, but ideally we want to have the text proofed next week so if you could please send me your comments/edits etc by Tuesday that would awesome and very much appreciated! Thanks!

cheapjack, 2015-04-17:
Ok Ive put all this text [here](https://github.com/cheapjack/buildyourown/blob/master/Exhibition/FACT/interpretation/MainTextPanelText.md) and started to edit it for next week. By then we will have run over things with Reach, pinged Enabling the future but would be good to have got in touch with Ultimaker so we could include their logo? @DefProc can we get in touch with them about this (think you have contact there) before we see them at Maker Faire next week?
 
Ive included tick boxes so that we can see whether the partners inclusion is ok to go. Logo folder needs populating

cheapjack, 2015-04-20:
Can we have a look at this tomorrow, im working elsewhere till evening its the draft of the exhibition panel, will try have another crack at it if I get some time in the morning; if we are directly referring to Norwich hackspace do we need their profile? I think not as this can take place at a modified panel their end? Comments welcome!

So [draft is here](https://github.com/cheapjack/buildyourown/blob/master/Exhibition/FACT/interpretation/MainTextPanelText.md)

amcewen, 2015-04-20:
I've added the DoES logo.  The text is looking good so far.  I wonder if we should include something to encourage people to donate to Reach if they want to help out financially?

almataki, 2015-04-21:
I think the text is looking good but it won't be possible to present it exactly in this format. All panels follow the same model stylistically:
Title (year), Artist, main text (2-3paras), additional credits in italics and relevant urls
We will not include the biogs in the panels but in the gallery guide - staple stitched booklet - which is going to be available for free as you enter the gallery. The guide will include the same text plus any relevant biogs. Would you mind if I edit the draft to reflect the layout of the exhibition graphics?

almataki, 2015-04-21:
I think it will look neater to include logos on a separate panel as in 'here is everyone behind this project'

almataki, 2015-04-21:
Hi again, so I tweaked the text a bit and structured it so it can be laid out like the other captions. What do you think? 

**Desktop Prosthetics (2015)**
DoESLiverpool: Ross Dalziel, Patrick Fenner and Adrian McEwen

DoESLiverpool presents an iteration of the open-source project Enabling the Future, a global network of passionate volunteers using 3D printing to give the world a 'helping hand'. Inspired by a local family who used DoESLiverpool's workshop to print hand parts independently, DoES has installed a ‘production line’ for prosthetic hands. They will be using 3D printing technology and the open-source "Raptor Hand" design, which was developed to make printing and assembly of the hand’s components easier for their makers and recipients.

*Desktop Prosthetics* aims to raise awareness of some of the more practical uses of 3D printing and demonstrates how collaborative communities like DoES and Enabling the Future work together - sharing skills and specialised knowledge to solve real problems.
*[Also add something for visualisation? – CC needs to confirm this]*

Over the course of the exhibition, DoES Liverpool will be working with Reach, the association for children with upper limb deficiency, to help a number of local children build and assemble a prosthetic device. DoES invite you to get involved in testing and building prosthetics, experiment and understand what prosthetics are and how access to rapid prototyping and open source digital making tools can help people make the world the way they want it. Check the events panel for more details on how to take part. 

*Developed with the support of Reach North West and E-nabling the Future* 

www.doesliverpool.com 
www.enablingthefuture.org
www.reach.org.uk 

[for gallery guide same as the above + biogs below]
**DoES Liverpool**
DoES Liverpool is a community of makers and entrepreneurs with a diverse range of skills and interests. It was founded by creative technologists and developers Adrian McEwen, John McKerrell, Hakim Cassimally, Paul Freeman, Andy Goodwin and Ross Jones with the intention to create a friendly environment to foster collaboration and support the growth of the region in a meaningful way – by doing. The community includes a co-working space, a workshop and an event hub. Any profit helps and sustains the community. www.doesliverpool.com  

**e-NABLE**
e-NABLE first began in 2013, consisting of about 300 people who owned 3D printers or who had design skills to share, and who wanted to help improve the first open sourced design for 3D printed hands that had been released online. They also wanted to help print and assemble free 3D printed prosthetic devices to anyone that reached out to them. Now, in 2015, their “matching system” has over 1000 recipients in various stages and 3000 registered volunteers, who all work to make more people’s lives easier thanks to 3D printed hands. www.enablingthefuture.org

cheapjack, 2015-04-21:
This looks good but I prefer the bullet points of what is DoESLiverpool though and not sure if we need to list the founders but I think @amcewen can speak more for DoES than me; what do you think? I wonder if we'd need to get someone from Enable to agree to this though and I dont think we have a direct contact yet

almataki, 2015-04-22:
@cheapjack and @amcewen I think bullet points will look odd when the rest is all text. Here is a page of how the gallery guide's pages are going to look like.
[image]

cheapjack, 2015-04-22:
Ok fair enough ive rewritten and included your text for @amcewen and @DefProc to look over
So have a [look here](https://github.com/cheapjack/buildyourown/blob/master/Exhibition/FACT/interpretation/MainTextPanelText.md)

almataki, 2015-04-22:
Thanks! I will forward it to my proof reader once @amcewen and @DefProc also look over. Do you think it's better not to include a biog for enable? since we have no contact with them. All text has been taken from their website so i can't see why they'd mind.

almataki, 2015-04-27:
In relation to the guide AES also suggested there is a page with one photo per project - see mock up below. Can we use Baylee's  photo for this? Of course properly credited and everything.
[image]

almataki, 2015-04-27:
Also the curators were keen that your voice is somehow captured in the exhibition. So we would like to print a quote by all artists – about 30words for each commission. Ideally something that brings alive your process. If answering a direct question helps, we thought maybe answering this ‘How collaboration and skill-sharing influenced your process in developing the work?’ or ‘Describe in a few words the processes that went into making the work?’ could be good starting points?
Might you be able to send me a combined quote/reply to one the questions this week?

Trying to reduce your workload, I was thinking that maybe we can use one of your answers to the questions by OPEN. For example,
"DoESLiverpool like many makerspaces and hackspaces, as an organisation we do not do projects in a sense, we simply help our community to realise their projects with the facilities we have. Our community is essentially anyone who wants to do something with us. "

What do your think?

cheapjack, 2015-04-27:
RE open and workload; exactly we are using those answers as a template FAQ which you can [see here](https://github.com/cheapjack/buildyourown/blob/master/FAQ.md)

cheapjack, 2015-04-28:
Hi just checking we are all happy with the exhibition panel text so far? Its [here](https://github.com/cheapjack/buildyourown/blob/master/Exhibition/FACT/interpretation/MainTextPanelText.md)

Also regards the voice of us I've added some more detailed stuff about maker spaces and responded @almataki question  "to describe in a few words the processes that went into making the work" at the bottom of the FAQ; ive just waded in on that one, please comment and edit if you want @amcewen @DefProc [have a look here](https://github.com/cheapjack/buildyourown/blob/master/FAQ.md)

amcewen, 2015-04-29:
The text looks great to me.  I made a minor tweak to remove the "North West" from "Reach North West" because (a) the NW bit is mostly a regional coordinator rather than a full office, and (b) we're also talking to Reach head office and will be aiming to hook up Norwich Hackspace with the local Reach coordinator there.

amcewen, 2015-04-29:
The FAQ looks good (and we'll be continually updating it with new questions anyway).  I updated the link to Nesta's report as it's been published now.

almataki, 2015-04-30:
Hi guys and thanks for looking through the texts. I had the text proofed and my proof reader sent the following comment:
"I've just been having another look at the e-NABLE website and it looks to me as though e-NABLE is the official organisation name and Enabling the Future is more a kind of tag line. So I think perhaps it would be better to go with e-NABLE throughout. What do you think?"
I have to say the two names have been confusing when we talk about the project and I agree with her that we should choose one way of referring to e-nable throughout. do you see any issue with that?

cheapjack, 2015-04-30:
Well spotted and I'd agree with that. @DefProc has had some contact with them so will follow that up with him and get in touch with them asap. Im sure it will be fine to take from their pack but we should get some direct contact and thats admittedly well overdue

almataki, 2015-05-01:
Great! text and quote are signed off so have been sent to the proof reader to ensure coherence throughout the exhibition.
The last thing for the interpretation is the photo for the guide. Is it OK for us to use Baylee's photo?
Thanks!

amcewen, 2015-05-02:
Assuming you mean this photo - https://github.com/cheapjack/buildyourown/blob/master/RaptorHandBeingWorn.jpg - then yes, that's fine.  Just needs to be credited to Jason Abbott.

almataki, 2015-05-05:
Yes that's right! will make sure it's credited!

almataki, 2015-05-05:
I just saw your comment about the raptor hand. I added the line to the exhibition text below. Today and tomorrow is the very last opportunity for any changes to the exhibition text. In practice we can only add rather than edit as the text has already been proofed.
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

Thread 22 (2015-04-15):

cheapjack/buildyourown #22: Additional Interpretation

almataki, 2015-04-15:
I understand that additionally to the gallery interpretation #21  you are keen to have explanation texts around the printers, prosthetic components etc. It makes sense that there is more explanatory text around your display as it is quite different to everyone else's but as you can also imagine we have to ensure that the exhibition has a coherent look to it. So a couple questions in relation to this.
Where you planning to design these graphics yourselves?
How were you thinking of presenting them?

amcewen, 2015-04-19:
I don't think we've got as far as working out exactly how we're going to do that yet :-)

However, we should be able to produce something similar to the panels you're doing for the rest of the show.  Will you be able to share the source files, and/or details of things like the fonts used?  Then we can use them as a basis for ours.

It'll probably be 1.5mm acrylic rather than 3mm, but we can laser-etch that in-house - https://www.flickr.com/photos/amcewen/16215574363/ shows an example I made that way recently.  Obviously that's black text on white, whereas for the exhibition it would be the other way round, but that's just a case of buying the right laminate acrylic :-)

almataki, 2015-04-21:
I don't think this element should use the same design as the exhibition design, I'd be keen that it is distinct from the overall design and provided a cohesive visual identity to your project/area. 
However it is also important it doesn't clash with everything else so maybe we can chat about it once you know what type of info you want to include? Wasn't there an idea originally to use vinyls for this? It would also be nice to include An Endless Supply in this discussion.

almataki, 2015-04-22:
I spoke to Robin from An Endless Supply for the additional interpretation and they're happy to work on this so they have an overview of the overall exhibition aesthetic- of course all in discussion with you. When do you think you'll know the extend of the copy for this?

almataki, 2015-05-14:
Hi guys please see below the spread for Desktop Prosthetics from the latest gallery guide design. The exploded view looks good!
[image]

cheapjack, 2015-05-21:
@almataki looks great any chance you can get me the original How to artwork and font so we can match it on the sub-plinth? Ideally in some kind of editable vector format?

LesleyTaker, 2015-05-21:
This might also be a good time to talk about the Ultimaker logo etc which Daniel mentioned in his email to @DefProc and you guys? Could do it at the same time?

cheapjack, 2015-05-22:
Hi it may make sense to use the pegboard area around the printer station to display their logo: then we don't need an exact match to the formatting of the main interpretation and then it's clear what they are supporting.

Also need the BYO font still if anyone has it :)

almataki, 2015-05-22:
will get that to you Ross! sorry for the delay, I've asked Robin to send it over.

almataki, 2015-05-26:
Hi and sorry again for the delay. I had a chat with Robin and we think that rather than trying to match the exhibition design it makes more sense for the instructions to be designed in your own style so it is distinct to the rest and specific to your project. I need however to ask you to please share them with me before you print them on vinyl, just for us to have the general overview of the display. Hope that makes sense. Thanks!

cheapjack, 2015-05-26:
Ok well will just choose a generic font then. But it will mean it's the only different font if you dont mind. Will pick something like arial or one of these http://openfontlibrary.org

almataki, 2015-05-26:
Yes one of these will look good!

LesleyTaker, 2015-05-26:
I love Glacial Indifference. Mostly for the name...

-- 

Lesley Taker
Curatorial Co-ordinator
FACT (Foundation for Art and Creative Technology)
88 Wood Street
Liverpool, L1 4DQ

Please note, I am only in office until 3pm on a Friday.
tw: @lexy_taylor
t: + 44 (0)151 707 4419
f: + 44 (0)151 707 4445

http://www.fact.co.uk
Admin: +44 (0)151 707 4444
Bookings: +44 (0)871 902 5737

*FACT - Bringing people, art and *
*technology together since 2003*

--------------------------------------------------------------
--------------------------------------------------------------

*Build Your Own: Tools for Sharing4 June – 31 August*

Showcasing four new commissions that span different

models of creative practice, including art, craft, and

creative technology, *Build Your Own* celebrates a new

spirit of generosity through making from your local

street to global maker networks.

--------------------------------------------------------------
--------------------------------------------------------------

closed 2015-07-01 by cheapjack

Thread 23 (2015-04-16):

cheapjack/buildyourown #23: Workshop/events programme

amyjones, 2015-04-16:
Hi all, 

Just want to go through what the suggested dates for workshops would be from our side:  

June 5th:   Artist Talks (representative(s) from DoES) 

June 6th:  Measuring workshop - We do have another workshop on this day but I don't see that being an issue and understand it's important to get this process started asap.  

June 13th:   I'd like to recommend this for the prosthetics workshops as there is a conflicting workshop on June 20th.  Can you let me know asap if the 13th?  We may still be able to get it in the brochure before it goes to print if you let me know today! 

Assembly workshop Saturday 18th July & Saturday 15th August
TBD:  These look fine for now.  I'm compiling a Public Programme calendar today so we should get a better sense of what will fit best in July and August - will get back to you to 100% confirm!  

For now can you just confirm the dates of 5th, 6th and 13th June are workable from your side?  

Thanks so much! 

Amy

cheapjack, 2015-04-16:
Amy have a look at [the event page](https://github.com/cheapjack/buildyourown/tree/master/events) I've placed all the dates there and drafting the copy for each one in folders for each kind of event

Sorry not enough of us can manage the 13th: we've now suggested the 21st on the Sunday for the [What's Your Super Power: Prosthetic Hack](https://github.com/cheapjack/buildyourown/blob/master/events/prostheticshack/ProstheticHack.md); would that work?

cheapjack, 2015-04-16:
I've also changed this issue so it sounds more like a task that we can tick off and resolve rather than just an area of activity that needs to be thought about :)

amyjones, 2015-04-16:
Hi Ross,

Ok, I'm working around a jam packed programme here so excuse the back and
forth!! How does the following work:

Measuring workshop: Sat June 6th

Assembly workshops: 1st one - Sorry 18th not available so would you prefer
Sat 11th July or Sat 25th July?
2nd session -  Sat 15th August

Having the Prosthetic Hack day in June is going to be difficult - seems a
shame for it to share the audience with one of our other events and Sunday
is not a popular day for this kind of activity in our experience.  Below is
a selection of dates which would mean the event would get top billing!

Sat July 11th/25th (depending which you choose for the assembly workshop)
Sat 8th August
Sat 22nd August

Could you confirm a date for the first assembly workshop and for the Hack
day asap?

That's great about the copy for the measuring up and hack session, thank
you!  Do you have anything for the assembly workshops? Can't see it on
Github.

 I also need the following info from you:

   - Age suitability of each session (e.g 12+)
   - maximum number of participants per session
   - Detailed breakdown of the activity taking place in each session (inc.
   the duration of each element and breaks if required)
   - Times/duration of each session - our Saturday programme is typically
   12pm - 4.30pm
   - Location of workshops - are they ok to happen by your work in Gallery
   1?

I really need this by Monday at the very latest (ideally tomorrow!) if
we're to include the June activities in the Brochure.   Also, we'll need to
know the relevant logos/credits to be used in the Brochure.  Could you send
these through?

Sorry lots of questions/actionables in there!  Promise my messages will be
much shorter in the future!!

Amy

-- 

---
Amy Jones
Exhibition Coordinator
FACT (Foundation for Art and Creative Technology)
88 Wood Street
Liverpool, L1 4DQ

t: +44 (0)151 707 4403

www.fact.co.uk

Admin: +44 (0)151 707 4444
Bookings: +44 (0)871 902 5737
Information: +44 (0)151 707 4464

*FACT - Bringing people, art and *
*technology together since 2003*

--------------------------------------------------------------
--------------------------------------------------------------

*Group Therapy: Mental Distress in a Digital Age5 March – 17 May*

Originating from FACT’s extensive work within

mental health and wellbeing, the exhibition

explores the complex relationship between

technology, society, and mental health.

--------------------------------------------------------------
--------------------------------------------------------------

amcewen, 2015-04-16:
For future ref. everyone, this would've been better as comments on issue #6 - we can reopen closed issues if things change, and that would just keep all the event date discussion in one place.  (At least by mentioning it now there'll be a link between them :-)

cheapjack, 2015-04-16:
Ok I've considered clashes in all our personal diaries and DoES Events and the dates you suggest amy, so they are now updated [here](https://github.com/cheapjack/buildyourown/blob/master/events/README.md) and are:

 * [Measuring Up](https://github.com/cheapjack/buildyourown/tree/master/events/measuringupworkshop) **Saturday 6th June**
 * [What's your superpower? A Prosthetic Hack!](prostheticshack) **Saturday 25th July** 
 * Assembly workshop **Saturday 8th August** & **Saturday 22nd August**
 * TBD

@amcewen is following up on the other details @amyjones ta

amcewen, 2015-04-16:
Splitting the extra questions out into their own issues.  So the greater detail we'll need for the brochure is in issue #24 and then the stuff to work out nearer to the events running is in issue #25

amcewen, 2015-04-17:
I've spoken to Reach and those dates should be okay for them (no guarantees, but no obvious clashes :-)  Haven't been able to get in touch with Jason, but hopefully he'll be able to make them too.

cheapjack, 2015-04-17:
great

cheapjack, 2015-04-17:
Ive updated the event section dates, added some text and images if required and a tick box to tick when we are happy with it all

amyjones, 2015-04-20:
Perfect, thanks! Those dates are super.

-- 

---
Amy Jones
Exhibition Coordinator
FACT (Foundation for Art and Creative Technology)
88 Wood Street
Liverpool, L1 4DQ

t: +44 (0)151 707 4403

www.fact.co.uk

Admin: +44 (0)151 707 4444
Bookings: +44 (0)871 902 5737
Information: +44 (0)151 707 4464

*FACT - Bringing people, art and *
*technology together since 2003*

--------------------------------------------------------------
--------------------------------------------------------------

*Group Therapy: Mental Distress in a Digital Age5 March – 17 May*

Originating from FACT’s extensive work within

mental health and wellbeing, the exhibition

explores the complex relationship between

technology, society, and mental health.

--------------------------------------------------------------
--------------------------------------------------------------

amcewen, 2015-04-20:
Great.

closed 2015-04-20 by amcewen

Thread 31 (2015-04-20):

cheapjack/buildyourown #31: Order the additional parts we'll need to assemble the hands

amcewen, 2015-04-20:
Need to order the screws, elastic, velcro, padding, etc. that we'll need to assemble the hands.

Once we've decided on which hands we're building (issue #29) we can then work out what needs to be ordered and place the order.

We should get enough for ~30 hands (at least) as that should cover all we'll make in both Liverpool and Norwich.

amcewen, 2015-05-12:
@DefProc any chance you can work out what parts we need and get them ordered?  Jason donated some bits the other week, which are in his box in the workshop, so that might reduce what we need to order

DefProc, 2015-05-22:
Looking at the enable build list, and a trip round the internet, it looks like our shopping list is:

 * Tensioner Screws (100 will do 20 hands) M3 for small (1 scale) M4 for bigger (e.g. 1.25 scale) M5 for largest. We'll need one of each:
  * 100× M3×20mm Socket Cap stainless screws [ebay](http://www.ebay.co.uk/itm/201271005889?var=500469286553) - £3
  * 100× M4×25mm Socket Cap stainless screws [ebay](http://www.ebay.co.uk/itm/201271005889?var=500469286578) - £4.50
  * 100× M5×25mm Socket Cap stainless screws [ebay](http://www.ebay.co.uk/itm/201271005889?var=500469286620) - £6.50
 * 25m of 50mm wide Velcro One-Wrap (sew on, double sided, "hook and loop" tape). At 1.2m per hand, 25m will do 20 hands. Possible suppliers:
  * [ebay](http://www.ebay.co.uk/itm/Reusable-Hook-Loop-Strapping-Cable-Tie-VELCRO-Brand-One-Wrap-/250789282165?pt=LH_DefaultDomain_3&var=&hash=item3a6434c175) £50
  * [scf supplies](http://www.scfsupplies.co.uk/-One-Wrap-50mm-x-25-Metres/421.htm) - £50
  * [john downes](http://www.johndowns.co.uk/index.php?main_page=product_info&cPath=29_31&products_id=155) - £50
  * [fosseway tapes](http://www.fossewaytapes.co.uk/Self-Adhesive-Velcro-%C2%AE-Brand-Tapes/Self-Adhesive-50mm-2inch-X-25m-VELCRO-%C2%AE-Brand-tape.html) - £55
 * 5mm thick, adhesive backed, closed-cell, firm polyethelyne foam, e.g. Plastizote LD45 (EFP30, Northfoam 170, Plastiozte LD33 (softer) may work as alternatives). Approx 450cm^2 required per hand (40 per 1×2m sheet). Possible suppliers:
  * [easy foam (Simply Foam Product Ltd)](http://www.easyfoam.co.uk/zotefoam-plastazote.php) - £31 for LD33
  * [efoam (Simply Foam Products Ltd)](http://www.efoam.co.uk/closed-cell-polyethylene-foam.php) - £26 for EFP30
 * Spectra/Dyneema/UHDPE braided line >0.5mm diameter, 2.5m per hand. 
  * [ebay](http://www.ebay.co.uk/itm/1000M-100LB-Fishing-Line-Dyneema-Braided-Super-Strong-4-Strands-UK-Delivery-/151497675520) - £16 for 1000m
 * 2mm diameter elastic, "shock" cord, 1.5m per hand. Possible suppliers:
  * [ebay](http://www.ebay.co.uk/itm/ELASTIC-BUNGEE-ROPE-SHOCK-CORD-BLACK-WHITE-RED-BLUE-2mm-3mm-4mm-5mm-6mm-8mm-10mm-/201240391374) - £14.50 /100m
  * [ebay](http://www.ebay.co.uk/itm/ELASTIC-BUNGEE-ROPE-SHOCK-CORD-TIE-DOWN-BLUE-2mm-3mm-4mm-5mm-6mm-8mm-10mm-/3611498834010) - £14.50 /100m, £20 /150m

That puts us around £125 for a set of parts to cover at least 20 hands. 

Any notes, observations, objections? I haven't ordered anything yet.

amcewen, 2015-05-22:
How much braided line do we need?  Jason has donated the reel he used, which is Rovex Depth Finder braid line - 45.4kg (strength, not weight of line :-) 0.5mm, 270m (less however much one hand is)

Otherwise, that looks good, presumably optimising for quick delivery given our timescales...

DefProc, 2015-05-25:
270m minus one hand, will still leave over 100 hands-worth (assuming the 2.5m/hand is accurate).

amcewen, 2015-05-26:
Bah.  Managed to accidentally order the braided line too.  Still, everything has been ordered.  We'll need some more foam, but we can see what the stuff we'd ordered is like before ordering more.

Will close this once everything has arrived.

LesleyTaker, 2015-05-26:
Nice one!!

-- 

Lesley Taker
Curatorial Co-ordinator
FACT (Foundation for Art and Creative Technology)
88 Wood Street
Liverpool, L1 4DQ

Please note, I am only in office until 3pm on a Friday.
tw: @lexy_taylor
t: + 44 (0)151 707 4419
f: + 44 (0)151 707 4445

http://www.fact.co.uk
Admin: +44 (0)151 707 4444
Bookings: +44 (0)871 902 5737

*FACT - Bringing people, art and *
*technology together since 2003*

--------------------------------------------------------------
--------------------------------------------------------------

*Build Your Own: Tools for Sharing4 June – 31 August*

Showcasing four new commissions that span different

models of creative practice, including art, craft, and

creative technology, *Build Your Own* celebrates a new

spirit of generosity through making from your local

street to global maker networks.

--------------------------------------------------------------
--------------------------------------------------------------

DefProc, 2015-05-28:
In an off-by-one error, we will also need some self-tapping screws for palms. Which I need to size.

amcewen, 2015-05-29:
Still waiting on the M4 and M5 screws, but everything else has arrived

LesleyTaker, 2015-06-01:
Know when they'll get here?
L

-- 

Lesley Taker
Curatorial Co-ordinator
FACT (Foundation for Art and Creative Technology)
88 Wood Street
Liverpool, L1 4DQ

Please note, I am only in office until 3pm on a Friday.
tw: @lexy_taylor
t: + 44 (0)151 707 4419
f: + 44 (0)151 707 4445

http://www.fact.co.uk
Admin: +44 (0)151 707 4444
Bookings: +44 (0)871 902 5737

*FACT - Bringing people, art and *
*technology together since 2003*

--------------------------------------------------------------
--------------------------------------------------------------

*Build Your Own: Tools for Sharing4 June – 31 August*

Showcasing four new commissions that span different

models of creative practice, including art, craft, and

creative technology, *Build Your Own* celebrates a new

spirit of generosity through making from your local

street to global maker networks.

--------------------------------------------------------------
--------------------------------------------------------------

cheapjack, 2015-06-01:
Not sure but we will have enough parts and replacement screws to be getting on with aside from nice gel grips that Baylee's dad is getting for us

amcewen, 2015-06-02:
We've got enough to assemble the hands we need for the launch, so moving this to the first assembly day milestone as that's when we'll need the rest of stuff.

amcewen, 2015-06-02:
Reopening this until we have received all the parts we've ordered.

amcewen, 2015-07-30:
Given some of the hands are smaller, I've ordered 20m of 1mm shock cord to make them easier to assemble.

@DefProc Are we happy with the foam we got?  IIRC we didn't buy the full amount as you wanted to check it was suitable.  Is it suitable?  Do we need to buy any more?

DefProc, 2015-08-03:
Yes, I'm happy with the foam. Although it's not a medical grade (there's 
no test for allergic reactions or limit on the ingredients for long term 
use next to skin), it was a good thickness and good firmness, and is 
suitable for this short term, testing, experimentation use.

Yes, we'll need some more. Another 3-4 strips should be plenty.

amcewen, 2015-08-03:
More foam ordered.

marionofnorwich, 2015-09-14:
Hello guys
Is there any kind of review or update on this list now that the project has run in Liverpool?
Marion

cheapjack, 2015-09-14:
We need to do another audit of the non-3d Printed parts that norwich may require to prevent needlessly buying things twice eg. I think we have plenty of velcro and let Marion know about it. We have started a Norwich box in the workshop at DoES for everything we need to send them.

cheapjack, 2015-09-14:
@marionofnorwich we will update the list this week, see my previous comment & email :+1:

marionofnorwich, 2015-09-14:
Thanks @cheapjack . Do you think that there is any mileage in us speaking with Jason? Drew really helpful but doesn't have time to come to Norwich I don't think. Any tips on the functionality would help, though really good talking to Drew in terms of expectations of the Raptor

closed 2015-10-26 by cheapjack

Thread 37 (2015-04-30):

cheapjack/buildyourown #37: Organise a date for Front of House training

LesleyTaker, 2015-04-30:
I am getting the team trained in basic 3D Printing using the UPs, through Mark Wright and Jon Couch who has already received training, but it would be better if we could do some specific training for the Ultimakers and your project, if that seems do-able? Would you guys like to recommend some dates one, or more of you might be able to do? Jon C will facilitate it and support you and we could use the Media Lab here, or send them down to DoES- whatever you think.

cheapjack, 2015-04-30:
Once we know delivery times of the Ultimakers we can set this date; would make sense if they came to DoES as we will be testing and preprinting stuff for the show great idea. Will have to get ourselves up to speed also!

LesleyTaker, 2015-04-30:
Sounds good to me, just let me know!! I am arranging some general 3D
training, probably on 30th May because that's just after our next volunteer
intake and general FACT training, but can move this earlier if necessary?

-- 

Lesley Taker
Curatorial Co-ordinator
FACT (Foundation for Art and Creative Technology)
88 Wood Street
Liverpool, L1 4DQ

Please note, I am only in office until 3pm on a Friday.
tw: @lexy_taylor
t: + 44 (0)151 707 4419
f: + 44 (0)151 707 4445

http://www.fact.co.uk
Admin: +44 (0)151 707 4444
Bookings: +44 (0)871 902 5737

*FACT - Bringing people, art and *
*technology together since 2003*

--------------------------------------------------------------
--------------------------------------------------------------

*Group Therapy: Mental Distress in a Digital Age5 March – 17 May*

Originating from FACT’s extensive work within

mental health and wellbeing, the exhibition

explores the complex relationship between

technology, society, and mental health.

--------------------------------------------------------------
--------------------------------------------------------------

amcewen, 2015-05-02:
Tweaked the title as that's what we want to sort out and arranging a date is just the first step on that.  Currently stalled on issue #2 as @cheapjack said (but now hopefully when that issue gets closed we'll spot that this one is freed up)

cheapjack, 2015-05-06:
Ok Im going to list some possible dates for training GA's, prob best in week its most likely to be set up ready to go 

Monday 1st June
* [x] @cheapjack
* [ ] @amcewen 
* [ ] @DefProc 

Tuesday 2nd June
* [x] @cheapjack
* [ ] @amcewen 
* [ ] @DefProc 

Wednesday 3rd June
* [ ] @cheapjack
* [ ] @amcewen 
* [ ] @DefProc

LesleyTaker, 2015-05-13:
Just to let you know, Front of House have said their preference would be Wed 3 June!

LesleyTaker, 2015-05-26:
Hey all, what date did we decide for this? Really need to book it in with the volunteers etc 
Thanks!!!

cheapjack, 2015-05-26:
Wednesday 3rd June will be fine for me and @DefProc (see above) and we wont need @amcewen for that session, just update us on the time. As we havent fixed the date on getting the Ultimakers installed and running in the space yet, Id suggest a time late afternoon on the 3rd June. @LesleyTaker could you let us know when that week you think space would be clear, safe enough and powered to setup and start printing? Im thinking Wednesday may be best; we dont want to install them too soon and not be able to print or interrupt prints so power will have to be fixed for us. Also gives us maximum time for any overnight prints we might need.

LesleyTaker, 2015-05-26:
Late on Tuesday (2nd) or Wednesday (3rd) morning would be fine to put them
in.

Do you want to do the training with them all installed or do training maybe
in another space then install them? Because that obviously affects the
timing of placing them etc. I assume it would be best to do it in situ?
With this in mind, let me know what time you'd to do the training. The
techs break for an hour for lunch at 1pm, and finish (theoretically) at
5.30pm, just FYI. But there shouldn't be that much to do on the Wednesday
anyway.

Will you guys have other (obviously smaller) hands ready so that people can
see / use them on the opening night? Just aware we will only like have one
from the Ultimakers...

-- 

Lesley Taker
Curatorial Co-ordinator
FACT (Foundation for Art and Creative Technology)
88 Wood Street
Liverpool, L1 4DQ

Please note, I am only in office until 3pm on a Friday.
tw: @lexy_taylor
t: + 44 (0)151 707 4419
f: + 44 (0)151 707 4445

http://www.fact.co.uk
Admin: +44 (0)151 707 4444
Bookings: +44 (0)871 902 5737

*FACT - Bringing people, art and *
*technology together since 2003*

--------------------------------------------------------------
--------------------------------------------------------------

*Build Your Own: Tools for Sharing4 June – 31 August*

Showcasing four new commissions that span different

models of creative practice, including art, craft, and

creative technology, *Build Your Own* celebrates a new

spirit of generosity through making from your local

street to global maker networks.

--------------------------------------------------------------
--------------------------------------------------------------

cheapjack, 2015-05-26:
No we need to do the training with them installed as that' s where they will be using them and will need to go through our system for keeping track of parts etc. Maybe 3pm would be ok: @DefProc? 

We are planning on printing one for the opening night aside from the vitrine display ones. Most likely one. It may be printed on the Ultimaker or the UP

LesleyTaker, 2015-05-26:
3pm sounds good, will wait for @DefProc sign off though. Is there any way
we can have one or two more printed in advance? Purely because people will
definitely want to pick them up, see how they feel etc, and it will be
super busy on the opening night.

-- 

Lesley Taker
Curatorial Co-ordinator
FACT (Foundation for Art and Creative Technology)
88 Wood Street
Liverpool, L1 4DQ

Please note, I am only in office until 3pm on a Friday.
tw: @lexy_taylor
t: + 44 (0)151 707 4419
f: + 44 (0)151 707 4445

http://www.fact.co.uk
Admin: +44 (0)151 707 4444
Bookings: +44 (0)871 902 5737

*FACT - Bringing people, art and *
*technology together since 2003*

--------------------------------------------------------------
--------------------------------------------------------------

*Build Your Own: Tools for Sharing4 June – 31 August*

Showcasing four new commissions that span different

models of creative practice, including art, craft, and

creative technology, *Build Your Own* celebrates a new

spirit of generosity through making from your local

street to global maker networks.

--------------------------------------------------------------
--------------------------------------------------------------

amcewen, 2015-06-02:
I've generated the files for another demonstration hand - checked into git as cad/hands/demonstration-85.

We should kick off printing that hand out on Thursday so the printers have something to run with during the first couple of days.  It will also let front-of-house run through the procedure for a print correctly too.

We can then assemble it during the workshop on Saturday (it'll help explain how things go together) and then be left for the public to try on.

DefProc, 2015-06-05:
train'd

closed 2015-06-05 by DefProc

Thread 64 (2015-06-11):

cheapjack/buildyourown #64: Empty seeming SD Cards [urgent]

LesleyTaker, 2015-06-11:
Hey, sorry if I've missed something but the printers are currently not printing anything, looks like they've completed everything that was on the SD cards. Sorry if this is something you told Mark / Jon - both of them are off today (Mark's off for ages) and I can't find anything in the other issues / guide other than a print queue looking sparse:
Are there any other cards anywhere, or do we need to queue stuff/ do you guys need to? 
Thanks
!!!

cheapjack, 2015-06-11:
Hi Lesley 
The outcome of Saturday was that many children participation turned out not to have working wrist joints to make the Raptor reloaded the best design for their situation. So we are just trying to decide the best course of action. We will be contacting the families to explain this.

We populated the disks on the printer for this week to print a hand that was not affected by this but I see we must have completed this print by now.

We photographed and made measurements and notes for each participant on the workshop and in the case of Harrisson (a young lad all the way from Devon), he was happy experimenting with the raptor reloaded using his elbow joint, and took one home, which although not ideal did make him feel part of the project and they understood its limitations in relation to his situation. We need to work back through the notes that we made with Drew and work out the best responses for everyone which we've not had time to do yet. Options are so far;

1 Still print out Raptor Reloaded designs for everyone as planned and let families know that this model may not be the best design for them but is a starting point in a co-design process that we can build on in the subsequent workshops and at DoES as the interest group around the project grows

2 Print out alternative designs : they exist but we have no experience building or assembling or fitting them and unclear whether we would be able to make them a good fit for the participants remotely: so we could end up with prosthetics as problematic as a raptor for someone with no working wrist.

Meantime we should generate some more raptor files to cover the next few days: but I think option 1 now seems our best course of action. What do @amcewen @DefProc think? We talked about it yesterday and decided to delay decision and getting back to families to next week not realising prints would be complete by now. For time being/weekend we could print out another small demonstrator hand and Thwack hammer: so I can set one of those off tomorrow and explain to whoever is on.

LesleyTaker, 2015-06-11:
Oh god! Ok. Didn't know this was the case.

Do we really want to print out hands that these kids won't be able to use?
if we have their measurements how hard is it to adapt them to the other
models?

Maybe we can reach out (seriously no pun intended) to someone at Reach, or
someone who has more experience with a diverse range of hands to assist in
assembling etc? There's a bit of money left for their travel if we want to
go this way? It might be a good idea because then you guys are also
equipped to deal with a variety of hands if people come to use the
Ultimaker for their prosthetics?

This might be a rubbish idea, just thinking out loud.
Do you want me to come down for a chat tomorrow or something?

And nice one of the replacement demonstrator and the hammer, @cheapjack -
good call!

-- 

Lesley Taker
Curatorial Co-ordinator
FACT (Foundation for Art and Creative Technology)
88 Wood Street
Liverpool, L1 4DQ

Please note, I am only in office until 3pm on a Friday.
tw: @lexy_taylor
t: + 44 (0)151 707 4419
f: + 44 (0)151 707 4445

http://www.fact.co.uk
Admin: +44 (0)151 707 4444
Bookings: +44 (0)871 902 5737

*FACT - Bringing people, art and *
*technology together since 2003*

--------------------------------------------------------------
--------------------------------------------------------------

*Build Your Own: Tools for Sharing4 June – 31 August*

Showcasing four new commissions that span different

models of creative practice, including art, craft, and

creative technology, *Build Your Own* celebrates a new

spirit of generosity through making from your local

street to global maker networks.

--------------------------------------------------------------
--------------------------------------------------------------

-- 
 

*The contents of this email and any attachments are intended solely for the 
original recipient(s). If you have received it in error please contact the 
sender immediately by returning the e-mail or by telephoning a number 
contained in the body of the e-mail, then please delete the e-mail 
immediately without disclosing its contents. No responsibility is accepted 
for loss or damage arising from viruses or changes made to this message 
after it was sent. The views contained in this email are those of the 
author and not necessarily those of the authors employer or service 
provider.*

cheapjack, 2015-06-11:
We basically don't know how hard it would be to use the RIT Arm what the cad files are like or design it for the kids we met on Saturday. We will look into it for sure but meantime example hands could cover us temporarily so the exhibition is active. It's worth trying one out we've just not built in the time to do that yet.

Appreciate the suggestion Lesley but it ups the scope of the project a fair bit researching prosthetic 'experts' at this stage and working with Reach like that I think plus it was always a starting point what we were doing: I think the e-nable people would be more appropriate than reach: and Drew already helping: he has alot of experience and enthusiasm and is already helping us with this. If we could pay for Drew's travel to attend the assembly workshops and make the prosthetic hack day about this issue that's a good idea: though this is an additional cost to our original budget I guess.

We can get some elements printing and then come up with a considered solution. These were always going to be prototypes and it's a process so don't think we have to panic into a solution: I know you want the exhibition visibly printing but there is always down time when you prototyping things.

That said we do want to keep everyone informed and will draft something so all participants are aware of what we're doing next week.

I could pop in tomorrow morning and set off another demo hand and have a look over things.

cheapjack, 2015-06-12:
@defproc kindly generated some plates for a raptor gasp-law which will keep the prints active until Tuesday. I've suggested just running this on one printer on the right and leave plate 5 of guts-squid on display as it looks nice and explains process nicely

cheapjack, 2015-06-17:
We've populated the SD cards on the Ultimakers with ```Gin-Timers``` and ```Leaf-Keeps``` for those families who are best suited. We will continue to generate files for Raptor hands and transferring to SD card with a view to fitting and modding them at the Assembly workshops in August and the Prosthetic Hackday in July.

closed 2015-06-17 by cheapjack

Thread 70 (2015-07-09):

cheapjack/buildyourown #70: Support for Norwich

marionofnorwich, 2015-07-09:
Just trying out how to communicate via Github. Just to say that we have printed a hand down here but have no assembly materials as yet. Hoping to sort that out soon

almataki, 2015-07-09:
@marionofnorwich well done for printing the first hand!!

marionofnorwich, 2015-07-09:
Thanks Alma. Once of our members has an Ultimaker and kindly printed two off actually, one small, one large so we at least have something to play with!

amcewen, 2015-07-14:
Cool that you've got some hands printed to try out.

I gave @marionofnorwich some padding, velcro, fishing line and elastic when she called in on Saturday, so hopefully they'll be up and running on getting the hands assembled now.

closed 2015-07-14 by amcewen

marionofnorwich, 2015-07-14:
Yes, we had a go at assembling last night but the elastic is too thick to go through the holes on the small size hand we printed so need to look for thinner elastic. The larger hand we need more parts for as was only part printed

amcewen, 2015-07-15:
If you need pointers on where to get bits, there's a list of links for where we got stuff in issue #31

marionofnorwich, 2015-07-15:
Yes, thanks Adrian

DefProc, 2015-07-18:
We got 2mm diameter elastic, but I actually like 1mm better — especially for the smaller builds.

marionofnorwich, 2015-07-18:
Yes I think it would be much better for us too. Was it easy to get hold of?

DefProc, 2015-07-18:
I got our 2mm from ebay in a roll. 1mm was available too.

marionofnorwich, 2015-07-19:
Thanks. I have mocked up this flyer to recruit people to the first workshop, though it doesn't mention dates. Thought if I can get people to get in touch i can explain what's needed and when it is. Or could put more info on a second page/reverse. What do you think?
[image]

LesleyTaker, 2015-07-20:
Hey Marion
,
Just a few quick things!

   - FACT Liverpool should be FACT (Foundation for Art and Creative
   Technology) in the credit bit
   - No "the" before Crafts Council
   - Liverpool DoES should be DoESLiverpool (one word)
   - *Build Your Own: Tools for Sharing* (needs second part of title) and
   should be italicised
   - Probably good to mentioned Enable in there somewhere?

Also, I would change the bit where it says the Hackspace and DoES have
co-produced the exhibition, maybe put it in another location and have '*Desktop
Prosthetics* facilitated by' / 'co-ordinated by' or even credit as artists.
Up to you guys really!

Best,
L

-- 

Lesley Taker
Curatorial Co-ordinator
FACT (Foundation for Art and Creative Technology)
88 Wood Street
Liverpool, L1 4DQ

Please note, I am only in office until 3pm on a Friday.
tw: @lexy_taylor
t: + 44 (0)151 707 4419
f: + 44 (0)151 707 4445

http://www.fact.co.uk
Admin: +44 (0)151 707 4444
Bookings: +44 (0)871 902 5737

*FACT - Bringing people, art and *
*technology together since 2003*

--------------------------------------------------------------
--------------------------------------------------------------

*Build Your Own: Tools for Sharing4 June – 31 August*

Showcasing four new commissions that span different

models of creative practice, including art, craft, and

creative technology, *Build Your Own* celebrates a new

spirit of generosity through making from your local

street to global maker networks.

--------------------------------------------------------------
--------------------------------------------------------------

-- 
 

*The contents of this email and any attachments are intended solely for the 
original recipient(s). If you have received it in error please contact the 
sender immediately by returning the e-mail or by telephoning a number 
contained in the body of the e-mail, then please delete the e-mail 
immediately without disclosing its contents. No responsibility is accepted 
for loss or damage arising from viruses or changes made to this message 
after it was sent. The views contained in this email are those of the 
author and not necessarily those of the authors employer or service 
provider.*

marionofnorwich, 2015-07-20:
OK, thanks Lesley, I will change where I can. Obviously limited space and the main point is to get some interest from the people that we need to get signed up. I will amend and repost

Sorry I missed you when I came to Liverpool last weekend, it was a snatched opportunity but useful to speak to Joan and check in with Adrian

marionofnorwich, 2015-07-20:
[image]

marionofnorwich, 2015-07-20:
Latest version
[image]

almataki, 2015-07-21:
I think this is good to go! looks good to me.

marionofnorwich, 2015-07-21:
Yes, I think so too. Will work with Amanda in next few weeks to work up a
press release but this will enable us to get going with recruitment
Thanks
Marion

Marion Catlin
3 Trowse House Cottages
Bracondale Millgate
Norwich NR1 2EQ

Telephone 01603 765353
Mobile 07946 261651

marionofnorwich, 2015-07-21:
Just agreed the loan of an Ultimaker for the summer hols from Create Education so that we can have a play!

marionofnorwich, 2015-07-22:
How long did you guys run your measuring workshop for?

cheapjack, 2015-07-23:
We ran it 12-4.30 you can see our timing activity plan here

https://github.com/cheapjack/buildyourown/blob/master/events/MeasuringUpWorkshop.md

marionofnorwich, 2015-07-23:
Thanks Ross, that seems about right. We are thinking 11-3pm as the museum closes at 4.30pm so that will give us time for overrun and clearup. Does that sound right to you? I just hpe it will also give people enough time to travel but as you did two sessions, I guess we can cover all travel considerations that way. We have our first candidate - actually someone I know. What I didn't know was that in the last few months he has suffered a neural problem which means he can't use his hand, and he is a guitarist. He is making the most of it but quite distressed as he can't play so it could be a good mission to get him playing. members are enthusiastic generally and Ultimaker are lending us a machine for the holiday arriving tomorrow. So it is moving forward. We also put in a funding bid for a lasercutter for the space so may be back for more advice if we are successful!

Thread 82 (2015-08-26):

cheapjack/buildyourown #82: The X/Y belts are loose on both Ultimakers

cheapjack, 2015-08-26:
Someone passing through the exhibition suggested we get some [spring tensioners](http://www.ebay.co.uk/itm/Timing-Belt-Tensioner-Spring-Nickel-Plated-RepRap-CNC-3D-Printer-/151692235115) to tighten the belts without having to change them as they are looking super loose.

Need to look at them before sending on to Norwich

DefProc, 2015-09-03:
I've checked on the Ultimaker forums and google images of the black slider blocks, and the doesn't appear to be any adjustment for the "long" belts on the UM2. 

The long belt I saw was loose on the lower (attachment) side, which couldn't have a tensioner attached, but the end pulley can be loosened to allow redistribution of the slack, and allow addition of a tensioner on the other side. 

Metal spring tensioners are likely to be the better choice, but I did find a couple of printable ones too: 

 * http://www.thingiverse.com/thing:19892
 * http://www.thingiverse.com/thing:118917

Where are the Ultimakers now?

cheapjack, 2015-09-04:
They are currently at FACT @muff7 printed the tensioners out and they seem to help so that's great ta :+1:

closed 2015-09-10 by DefProc

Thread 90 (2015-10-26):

cheapjack/buildyourown #90: Make some links to guidelines around the Experimental Raptor Wing

cheapjack, 2015-10-26:
Link to some guides to assembling and eventually re-sizing the raptor wing as part of the whole 'system'

cheapjack, 2015-10-26:
This is a rough guide I sent to Ana in Norwich which I can re-visit and turn into a .md guide

## Assembling a raptor wing

[image]

The Raptor wing is a work in progress from the e-NABLE forum below 

http://forums.enablingthefuture.org/viewtopic.php?t=53

We had to work out how it would assemble from this forum and had to play with a mix of screw lengths and widths etc. to put it together. 

It does help to see one assembled here for the left affected arm see above.

Key bit is working out how the actuator thread threads through the assembled parts and how the whipple tree works; it adaptively grips around the shape of an object so it grips in a different way.

https://github.com/cheapjack/buildyourown/blob/master/cad/src/RaptorWing/whippletree.stl

(see forum, its the bit between tensioner box and knuckle channels that turns the single actuator thread into a single one) 

I think we found that the whippletree needs to sit inside the tensioner 'box' (the tensioner with pins is replaced with a box that just makes a space for the whipple tree and thumb actuator thread); you can see the tensioner/screw endpoints are 'replaced' and moved into the cuff.

https://github.com/cheapjack/buildyourown/blob/master/cad/src/RaptorWing/box_left.stl

Then gauntlet connects to the elbow joint interface:

https://github.com/cheapjack/buildyourown/blob/master/cad/src/RaptorWing/elbow_joint_interface_left.stl

Threading wise 2 threads (one from whipple tree and t'other from thumb (green & orange in my image attached) go through the channel in the elbow joint interface and onward through the elbow joint ( https://github.com/cheapjack/buildyourown/blob/master/cad/src/RaptorWing/elbow_joint.stl
) then up into the cuff where there are 2 tensioner pins replacing the Raptor Hand tensioner block in the Raptor Reloaded Hand

Refer to the [images](http://forums.enablingthefuture.org/viewtopic.php?t=53) on the forum does help

This was all we had to go on the rest is trying it out Im afraid! It worked pretty well for one family. My enquiry in the forum about different files that would be better to edit and tweak in cad is on their radar so imagine Nick will get on to it when he can and maybe someone can look at that if necessary

Hope that helps for now.

amcewen, 2015-11-03:
In https://github.com/cheapjack/buildyourown/commit/f2880d773152709cd49673dfdb4de38a85b490bc I added the scale_wing script, which runs the same way as the scale_hand one but scales and sorts the files for the Raptor Wing

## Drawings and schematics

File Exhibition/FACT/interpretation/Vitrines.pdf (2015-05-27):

### Overall Table Size

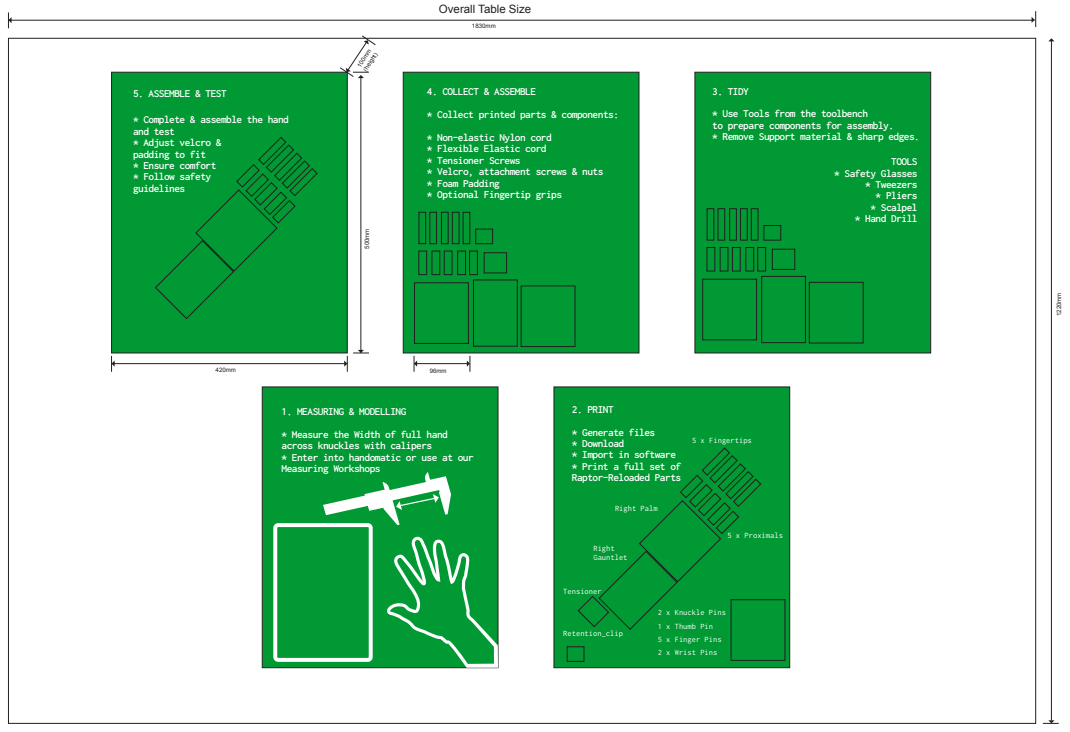
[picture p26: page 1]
100mm (height); 2. PRINT; 1. MEASURING & MODELLING; 3. TIDY; TOOLS * Safety Glasses * Tweezers * Pliers * Scalpel * Hand Drill; 5 x Proximals; 1 x Thumb Pin; 2 x Knuckle Pins; 2 x Wrist Pins; 5 x Finger Pins; 4. COLLECT & ASSEMBLE; 5. ASSEMBLE & TEST; Right Palm; Right Gauntlet; Tensioner; 5 x Fingertips; Retention_clip

* Collect printed parts & components:

* Use Tools from the toolbench
to prepare components for assembly.
* Remove Support material & sharp edges.

* Complete & assemble the hand
and test
* Adjust velcro &
padding to fit
* Ensure comfort
* Follow safety
guidelines

* Non-elastic Nylon cord
* Flexible Elastic cord
* Tensioner Screws
* Velcro, attachment screws & nuts
* Foam Padding
* Optional Fingertip grips

* Generate files
* Download
* Import in software
* Print a full set of
Raptor-Reloaded Parts

* Measure the Width of full hand
across knuckles with calipers
* Enter into handomatic or use at our
Measuring Workshops

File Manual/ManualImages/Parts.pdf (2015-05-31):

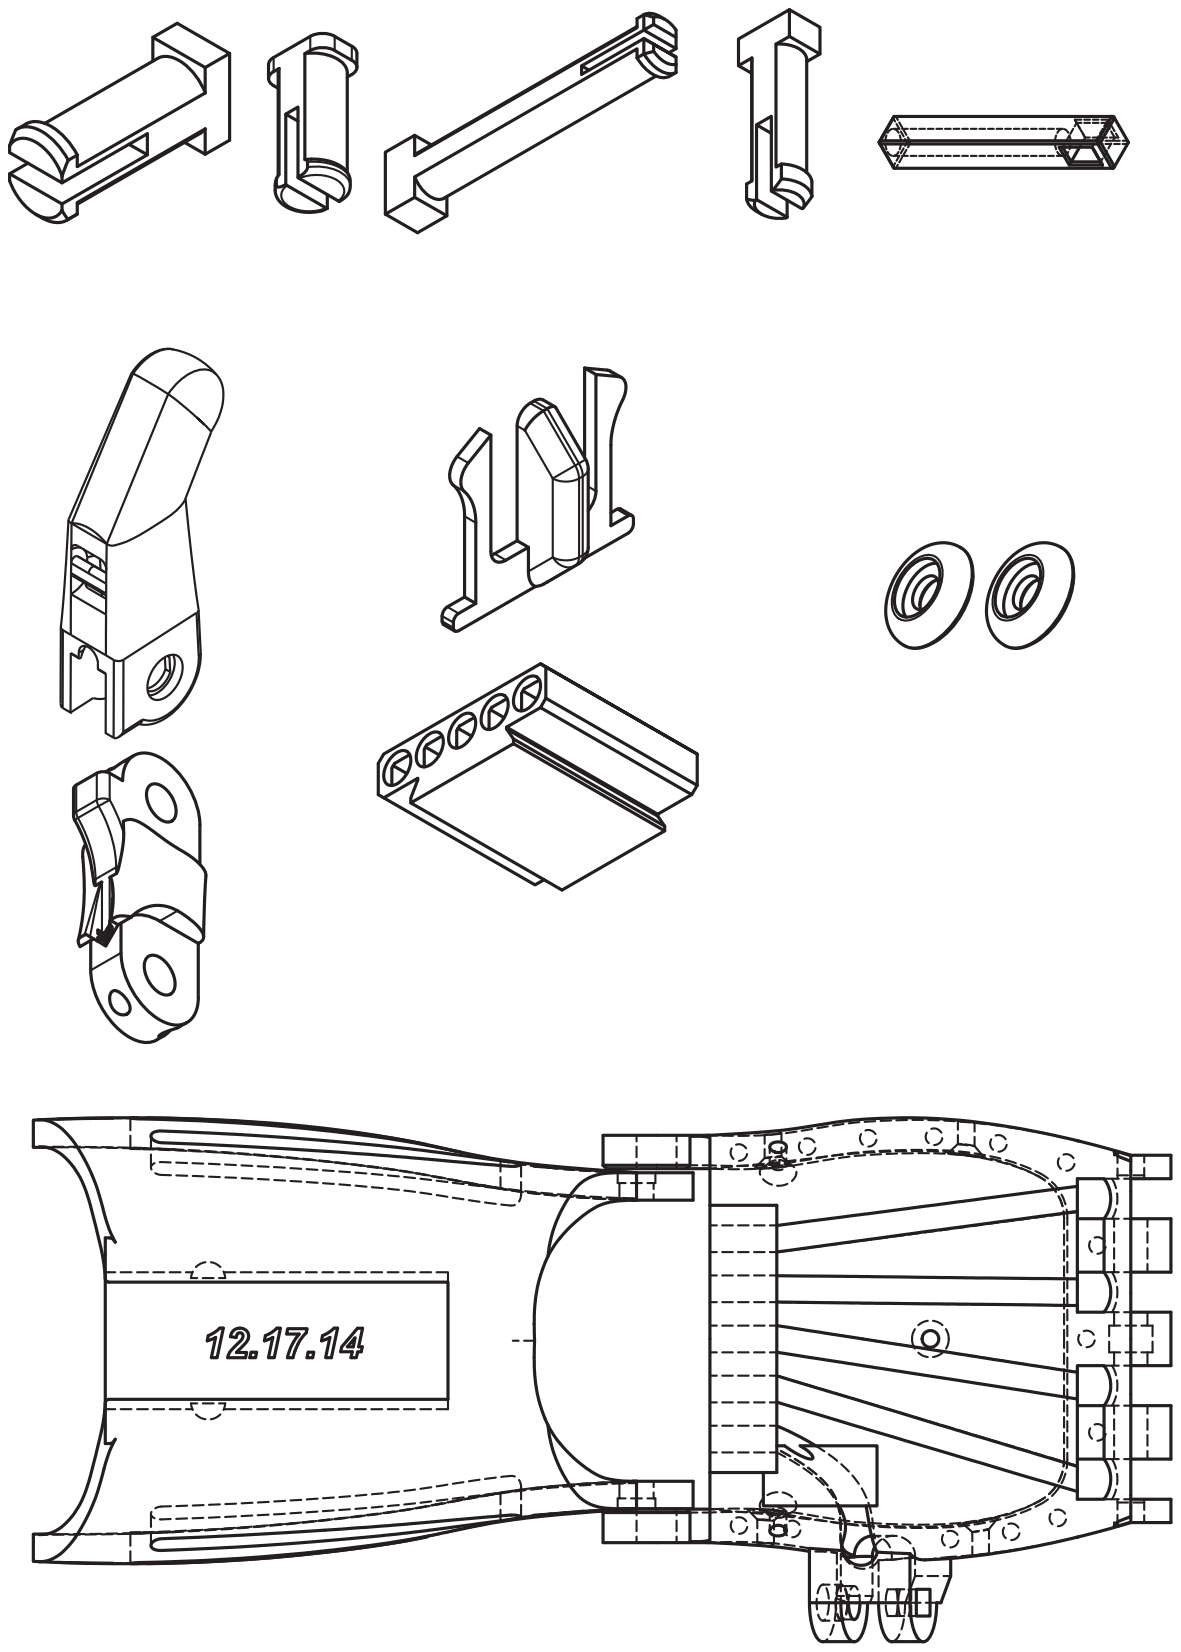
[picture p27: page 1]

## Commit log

2015-04-16 Create Assemblyworkshop
2015-04-17 Update Assemblyworkshop
2015-05-14 included scaling instructions straight from http://www.instructables.com/id/Assembly-of-e-NABLEs-Raptor-Reloaded-Hand/step1
2015-05-14 added raptor reloaded hands from eNable's thingiverse page
    [raptor_2.0_finger_pin.stl, raptor_2.0_fingertip.stl, raptor_2.0_proximal.stl, raptor_reloaded_fingertip_with_nail.stl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]
2015-05-14 first, hardcoded, scad files for resizing
    [raptor_2.0_finger_pin.scad, scaling.scad]
2015-05-15 added the current scad files for stls in this folder
    [raptor_2.0_fingertip.scad, raptor_2.0_proximal.scad, raptor_reloaded_fingertip_with_nail.scad, raptor_reloaded_gauntlet_supported.scad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]
2015-05-15 removed scale echo from openscad conversion
    [scaling.scad]
2015-05-15 passed the gauntlet through netfabb to remove build errors
    [raptor_reloaded_gauntlet_supported.stl]
2015-05-15 generated a set of stls for inital printing
    [raptor_2.0_finger_pin.stl, raptor_2.0_fingertip.stl, raptor_2.0_proximal.stl, raptor_reloaded_gauntlet_supported.stl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]
2015-05-18 break is unnecessary in a case statement
2015-05-27 Added vinyl cut files and test toolpaths
    [DoESLigoMinecraft.stl]
2015-05-28 Added files for a 90mm-span hand, for people to try out when visiting the exhibition
    [raptor_2.0_finger_pin.stl, raptor_2.0_fingertip.stl, raptor_2.0_proximal.stl, raptor_reloaded_fingertip_with_nail.stl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]
2015-05-28 removed fingertips with nails from the cad sources
    [raptor_reloaded_fingertip_with_nail.scad, raptor_reloaded_fingertip_with_nail.stl]
2015-05-31 corrected .stl→.st error on renumbering
2015-05-31 updated baylee's hand r.e. stl→st bug
    [raptor_2.0_finger_pin-1.stl, raptor_2.0_finger_pin-2.stl, raptor_2.0_finger_pin-3.stl, raptor_2.0_finger_pin-4.stl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]
2015-06-01 collects all the parts into folders ready for plating
    [HD_Font_Keychain_v4_0.scad, tag-1.stl, tag-2.stl, tag-3.stl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]
2015-06-01 regenerated baylee's hand parts
    [baylee.stl, raptor_2.0_finger_pin-1.stl, raptor_2.0_finger_pin-2.stl, raptor_2.0_finger_pin-3.stl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]
2015-06-02 changed default size to 65mm. closes issue #52
2015-06-02 Added generated files for the demonstration hands, as referenced in issues #20 and #37
    [demonstration-63.stl, demonstration-80.stl, demonstration-85.stl, demonstration-90.stl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]
2015-06-02 added tag hooks to plate 0
    [tag-hook-0.stl, tag-hook-1.stl, tag-hook-2.stl, tag-hook-4.stl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]
2015-06-03 added missing tag-hook-3 for plate 0
    [tag-hook-3.stl]
2015-06-04 regenerated demo-85 in red/silver
    [demo-85-1.stl, demo-85.stl, demonstration-85.stl, raptor_2.0_finger_pin-1.stl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]
2015-06-04 Started Print part of manual
2015-06-05 Updated the waiver of liability
    to include Health & Safety agreements and included all appopriate references to DoESLiverpool and FACT
    Ready for printing with [gitprint](https://gitprint.com/)
2015-06-05 Create Print Queue Template
    Example Print Queue Template for recording meaurement detail for [Measuring Workshop](
2015-06-05 Added Print Guidelines,
    Not complete
2015-06-06 Changed formatting better for printing in gitprint
2015-06-06 Changed formatting again for printing in gitprint
2015-06-06 added guts-squid
    [guts-squid-1.stl, guts-squid.stl, raptor_2.0_finger_pin-1.stl, raptor_2.0_finger_pin-2.stl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]
2015-06-08 lengthened the leader on the hook to hopefully lose less tags in the exhibition
    [hook-long-1.stl, hook-long-2.stl, hook-long-3.stl, hook-long-4.stl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]
2015-06-12 generated gasp-law hand
    [gasp-law.stl, hook-long-1.stl, hook-long-2.stl, hook-long-3.stl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]
2015-06-12 generated leaf-keeps
    [dkBlu-0-leaf-keeps.stl, dkBlu-1-leaf-keeps.stl, dkBlu-2-leaf-keeps.stl, hook-long-1.stl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]
2015-06-12 generated gin-timers
    [dkGra-3-gin-timers.stl, dkGra-4-gin-timers.stl, dkGra-5-gin-timers.stl, green-0-gin-timers.stl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]
2015-06-18 changed column title to make sure all printed
2015-07-02 generated gushes-eddy
    [hook-long-1.stl, hook-long-2.stl, hook-long-3.stl, hook-long-4.stl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]
2015-07-15 generated Mars-teeth
    [hook-long-1.stl, hook-long-2.stl, hook-long-3.stl, hook-long-4.stl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]
2015-07-15 generated ruing-beds
    [hook-long-1.stl, hook-long-2.stl, hook-long-3.stl, hook-long-4.stl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]
2015-07-15 generated manual-guts
    [green-3-manual-guts.stl, green-4-manual-guts.stl, green-5-manual-guts.stl, hook-long-1.stl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]
2015-07-15 generated tripe-keeps
    [dkBlu-3-trite-keeps.stl, dkBlu-4-trite-keeps.stl, dkBlu-5-trite-keeps.stl, hook-long-1.stl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]
2015-07-15 generated coil-leaf
    [blue-0-coil-leaf.stl, blue-1-coil-leaf.stl, blue-2-coil-leaf.stl, blue-3-coil-leaf.stl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]
2015-07-25 generated month-reared
    [any-0-month-reared.stl, any-1-month-reared.stl, any-2-month-reared.stl, any-3-month-reared.stl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]
2015-08-02 updated completed prints
2015-08-03 Made a more detailed plan for Assembly workshop
2015-08-15 Added RaptorWing/
    [box_left.stl, box_right.stl, elbow_joint.stl, elbow_joint_interface_left.stl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]
2015-08-15 Added re-print columns and deleted excess prints
2015-08-15 Hands that need reprinting because the initial versions were scaled using the wrong measurements. Fixes #72
    [Blue-0-peewee-undies.stl, Blue-1-peewee-undies.stl, Blue-2-peewee-undies.stl, Blue-3-peewee-undies.stl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]
2015-08-15 Added last three hands
    [Blue-0-grows-abort.stl, Blue-1-grows-abort.stl, Blue-2-grows-abort.stl, Grey-3-undies-manual.stl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]
2015-08-17 Added reprint codenames, removed reprinted column
    Because all the reprints have their own codename, the "Reprinted" column just duplicates the "All Plates Printed" column on the new codename hands, so best to remove it to avoid any confusion
2015-08-17 Moved pink/blue still-to-print to DoES Liverpool's queue
2015-08-18 Updated month-reared print
2015-08-23 Updated equipment list and clarified instructions after our assembly workshops
2015-08-23 Marked coil-Mars as completely printed
2015-08-25 Added wing-arm dir to cad
    [RITAssembled.scad, Retainer.igs, Retainer.ipt, Retainer.stp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]
2015-09-05 Updated the remaining in progress prints
    Refer to issue #85
2015-09-05 updated print queue at does
2015-09-14 Regenerated hands to use tweaked Cura settings (infill speed set to 0 so it matches overall speed, rather than set to 100)
    [Dark-Blue-3-gin-trite.stl, Dark-Blue-4-gin-trite.stl, Dark-Blue-5-gin-trite.stl, DarkBlue-3-gin-trite.stl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]
2015-09-14 Regenerated last three hands with slower infill speed
    [Blue-0-grows-abort.stl, Dark-Blue-0-eddy-troops.stl, Purple-0-beds-troy.stl]
2015-10-02 fixed #83 — scale hands checks wrist measurement
2015-10-02 fixed #87 — scaling factor now recorded in the settings file
2015-11-03 Add new scale_wing script to scale Raptor Wing files
    [box_left.scad, box_right.scad, elbow_joint.scad, elbow_joint.stl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]
2015-11-03 Add wing sized to match undies-manual.
    [Grey-0-troy-vane.stl, Grey-1-troy-vane.stl, Grey-2-troy-vane.stl, Grey-3-troy-vane.stl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]
2015-11-03 Add Raptor Wing sized for tuck-guts
    [box_left.stl, elbow_joint.stl, elbow_joint_interface_left.stl, tensioner_pin-1.stl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]
